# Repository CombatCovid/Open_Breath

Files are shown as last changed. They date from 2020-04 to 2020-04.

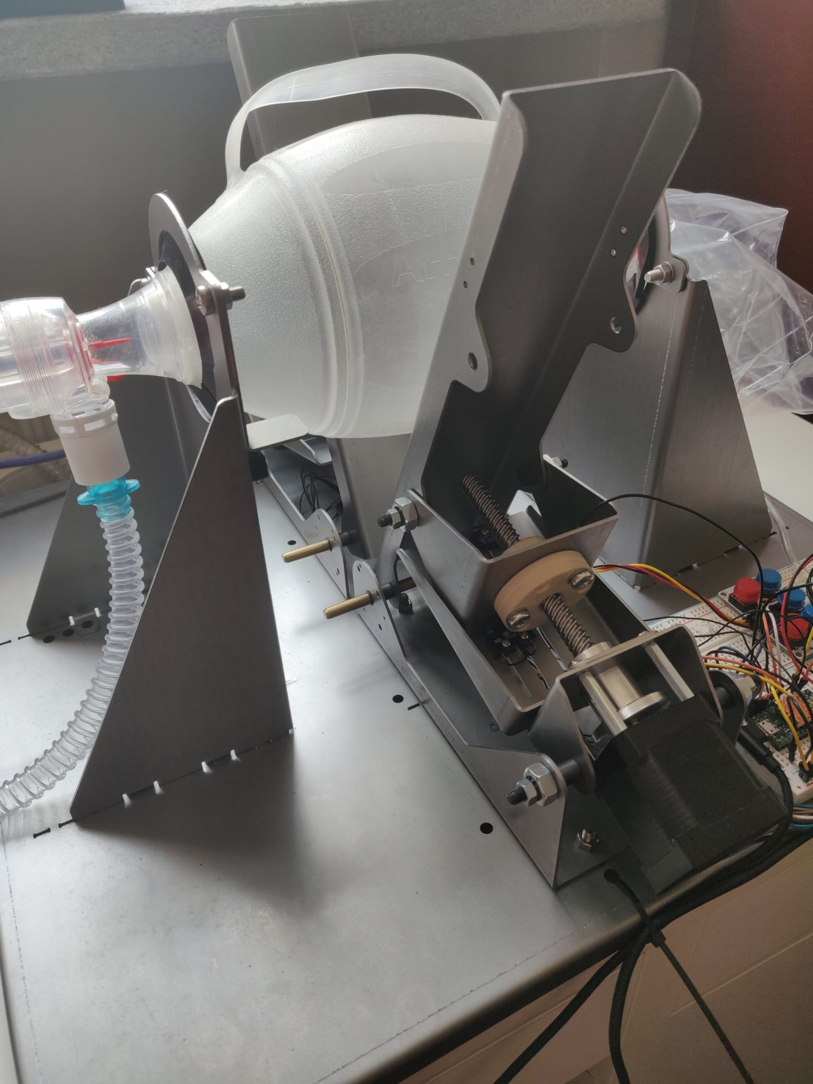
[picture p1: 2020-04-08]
docs/img/IMG-20200403-WA0022.jpg

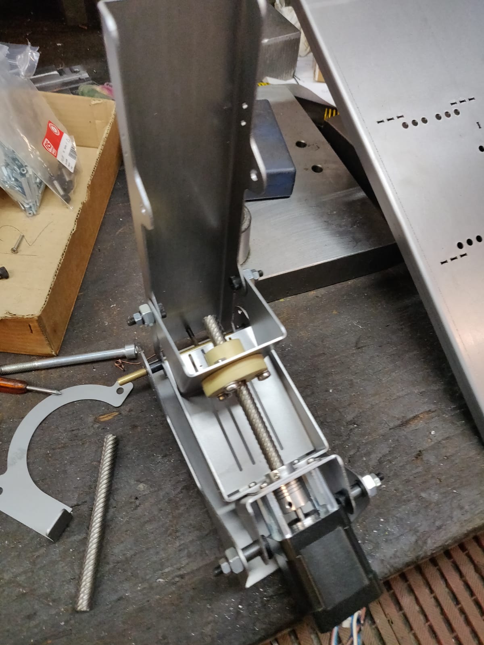
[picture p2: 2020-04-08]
docs/img/IMG-20200401-WA0078.jpg

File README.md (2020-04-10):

---
# n.b. metadata now goes in the metadata.yaml file, top level beside the repo README.md
---

# Title: OpenBreath Project



### References: 

All the information compiled here is from the [OpenBreath Project](https://www.openbreath.it/en/)

To download our repo: [**DOWNLOAD**](https://www.ohwr.org/project/openbreath/-/archive/master/openbreath-master.zip) <!-- Replace with github link -->

This is the url of our repo : [https://www.ohwr.org/project/openbreath/wikis/home/](https://www.ohwr.org/project/openbreath/wikis/home/) <!-- Replace with github link -->

### Background & Need

Open Breath project aims at the development and production of a scalable low-cost lung ventilator. Open Breath lung ventilator presents an innovative design, conceived to be quickly realized with off-the-shelflow-cost hardware components.

## Main Features
- Innovative design based on the automatization of a bag-valve-mask (BVM)
- Quickly producible with "off-the-shelf" parts
- Extremely low cost
- Both invasive and non-invasive assisted ventilation: PEEP, SIMV, CPAP modes
- Aims at compliance with the BS EN 80601-2-12:2020 standard
- Connected device and live interface:
- Sensors: pressure, flowrate
- Provides blood oxygenation rate and heart rate (nice to have)
- Will send alerts and updates in real-time directly to healthcare professionals
- We invite anyone who is interested to follow this work.

## Status of Development

The device is currently under development, a first metal prototype has been realized.



| Date   | Event |
| ----------- | ---------- |
| 01/03/2020  | Start of project in response to COVID-19 health emergency. Start on Openbreath.it  |
| 20/03/2020  | Need help from a Biomed apparatus certifier.  |
| 28/03/2020  | Need help from sheet metal workshop in and outside of Europe - first CAD Release Online  |
| 03/04/2020  | First Metal Prototype has been realized and the testing phase has started |

## How to replicate 

For assembeling the main body of the device sheet metal must be cut with a lasercutter and folded. 

DFX files for cutting can be downloaded [**HERE**](https://www.ohwr.org/project/openbreath/tree/master/CAD/DXF) <!-- Replace with github link -->

The hardware files for electronics can be downloaded [**HERE**](https://www.ohwr.org/project/openbreath/tree/master/Hardware) <!-- Replace with github link -->

The dashboard files can be download [**HERE**](https://www.ohwr.org/project/openbreath/tree/master/Dashboard) <!-- Replace with github link -->

<!-- # Steps to start documenting the equipment/design you found and chose 
[See this documentation example](https://github.com/CombatCovid/medical-shields-for-3d-printing). You can also download it to see the final result.
1. Download or clone this template to start documenting easily
2. Fill in the source files like STLS, CAD, etc inside

3. Use this one template to create new designs documentation
- Inside docs write down a simple README in language of choice.
- Put in the README.md the reference whre you got the source from to follow up.
- Write down steps to replicate if necessesary as well as guides in sequence.
If this part becomes difficult ask for help here in the [`#how-to-document-designs` channel ](https://discord.gg/QrAyWF)
 -->

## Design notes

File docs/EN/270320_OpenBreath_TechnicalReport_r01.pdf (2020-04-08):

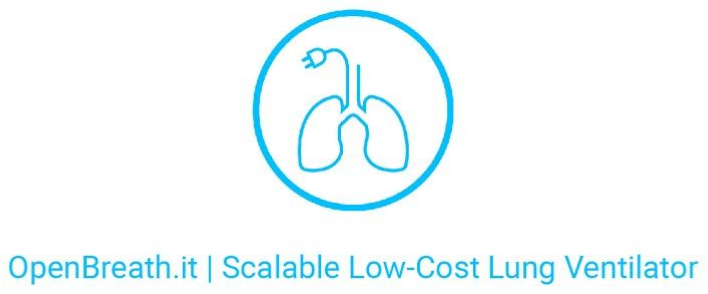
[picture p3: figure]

TOPIC: Technical Report_01 OpenBreath Device | 11:30 PM Friday, the 27th of March, 2020

This report aims to illustrate the features of the Open Breath lung ventilator, which is currently under

advanced development by our in-house team of designers and engineers. Being in the development

phase, the design may be subject to variations dictated by empirical requirements, which will be

established and proven as soon as possible by the in-depth testing phase of the device, and by the

public peer review phase.

The essential concept of the ventilator is the mechanical automation of a Bag Valve Mask (BVM), also

commonly known as Ambu® bag, a medical device used in manual resuscitation in hospitals all over

the world. We decided to use an Ambu bag as the pneumatic element of our ventilator for several

reasons. First of all, because of its proven operational effectiveness and its extensive availability as a

globally distributed, affordable component. It is also a certified medical device and can be easily

combined with all other medical devices needed to ensure proper patient ventilation.

The lung ventilator is composed of two identical and opposing four-link lever-screw mechanisms,

which synchronously compress an Ambu® self-expanding balloon (Fig. 1 label 6) equipped with a

PEEP valve. Each system consists of four laser-cut bent stainless steel plates (in fig. 1 labels 1, 2, 3,

4), a trapezoid screw (in fig. 1 label 2.c) and its lead nut (in fig. 1 label 3). a), a Nema 17 stepper

motor (in fig. 1 label 2.b) and two absolute or incremental rotary encoders, one axially positioned on

the motor shaft (in fig. 1 label 2.a) and the other one on the hinge of the presser (in fig. 1 label 5).

info@openbreath.it
www.openbreath.it

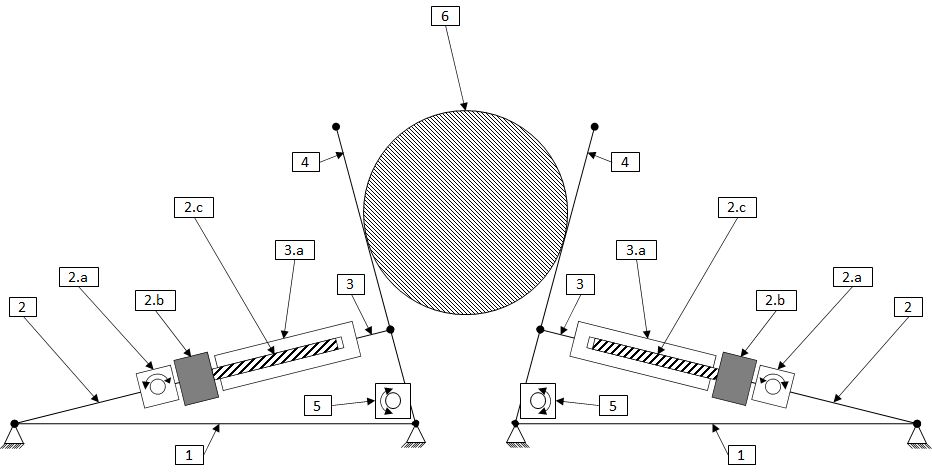
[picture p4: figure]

Figure 1.a - Scheme of the system in open position.

The encoders used can be both absolute and incremental according to the available supply. when incremental encoders are employed a homing operation will be carried out when the fan is switched on.

The stainless steel plates are hinged to each other by means of stainless steel pins and double flange IGUS technopolymer bushings, each axial sliding has a lifetime calculated by the manufacturer.

The trapezium screw and the lead nut are manufactured by IGUS, with calculated lifetime. The pressure application point of the lever-screw system is always tangent to the surface of the AMBU flask.

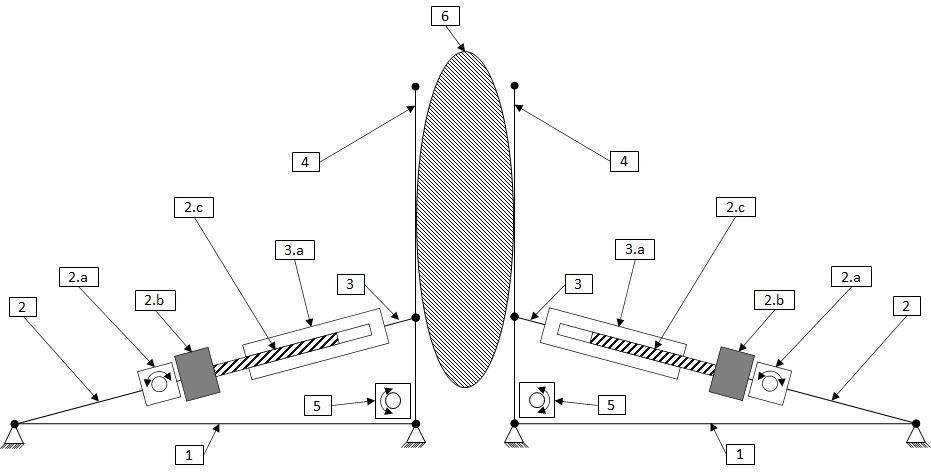
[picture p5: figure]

Figure 1.b -Scheme of the closed position systems.

The electronic system consists of a dual Motion Control (MC) system, a dual machine-operator interface system and a single embedded system used both for data display via web server and for alarm setting .

The single motion control system manages two stepper motors in open loop and supervises their movement by means of two absolute or incremental encoders, depending on the version in use. It also acquires pressure and air flow rate data via an I2C network.

The human-machine interface system takes care of acquiring the vital parameters from the operator and thereafter sends them to the motion control systems. Data is set by three incremental rotary encoders and a numeric keypad. The visualization is enabled by a LCD display, which includes an acoustic signal triggered by the set alarms.

The embedded system records all data, including the patient's vital parameters, and displays them on a web server application accessible from any device equipped with an internet browser (smartphones, tablets or PCs). In addition to this, it is possible to set alarms that will eventually be signalled both by the human-machine interface (HMI) and by the control panel hosted on the web server itself.

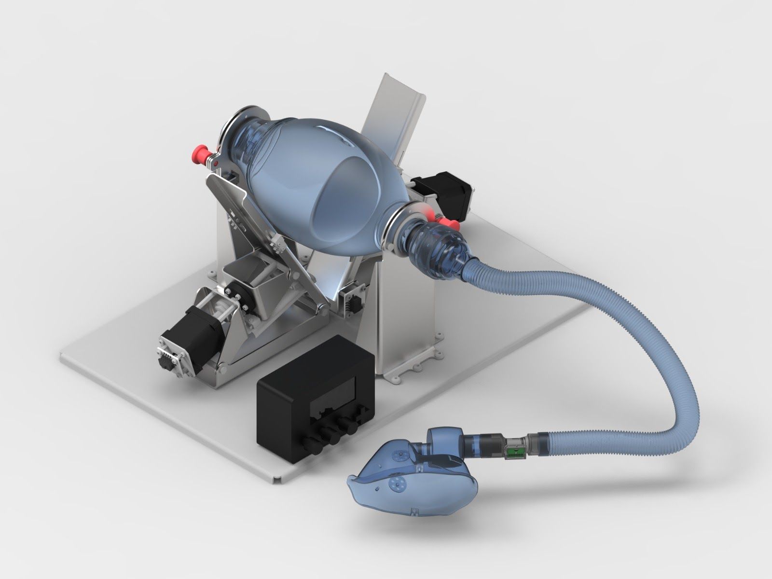
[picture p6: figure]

Fig. 2 - Overview, mechanics without external case.

M.C. systems, human-machine interface systems and sensors are completely redundant in all their components. This means that, in case of anomaly or failure of one of the boards, the remaining one takes absolute control over the system, guaranteeing its correct operation and immediately alerting the operator, who must promptly proceed to replace the ventilator.

In case one of the stepper motors fails, this will be deactivated, while the other one will increase the excursion and the speed of movement in order to keep the vital parameters output, set by the operator, unchanged. Contextually, the HMI system will warn the operator, who must replace the ventilator as soon as possible.

The motion control system acquires data from a pair of differential pressure sensors and a pair of flow meters, then compares the data of each pair and verifies that there are no discrepancies; otherwise, the HMI system will warn the operator.

The motion control system checks the effectiveness of the mechanical system by comparing the values of the encoder positioned on the motor shaft with those of the encoder positioned on the hinge shaft of the presser: if the deviations between the two values are too large, the HMI system warns the operator of a possible imminent mechanical fault.

The motion control system also regulates the air supplied to the patient according to two control modes:

1. CONSTANT PRESSURE:

The two pressors will compress the Ambu bag until the pressure threshold, set by the operator, is reached. A cut-off volume can also be selected at operator's discretion, when that level is reached, the ventilation cycle will be terminated.

2. CONSTANT VOLUME:

The two pressors will compress the Ambu until the volume threshold, set by the operator, is reached. A cut-off pressure can be selected at operator's discretion, when that level is reached, the ventilation cycle will be terminated.

These two control modes can be applied in two ventilation modes:

A. FULLY AUTOMATIC BREATHING:

In this mode, the frequency of ventilation is selected by the operator because the patient is unable to breathe independently.

B. ASSISTED RESPIRATION:

This mode of operation constantly monitors the flow of air-oxygen through flow meters. The patient's autonomic breathing is detected by increasing the monitored flow. When this occurs, the respirator pressors will compress the Ambu until the set pressure is reached and controlled by the pressure transducers.
When the motion control system detects a decrease in flow and a subsequent reversal of flow, the respirator goes into exhalation.

Positive end-expiratory pressure (PEEP) is regulated by a mechanical medical valve located near the Ambu outlet.

At this stage of development, the concentration of oxygen in the air supplied to the patient can be selected in three different sizes in this way:

- the concentration will be between 90% and 100% when using the Ambu with réservoir and oxygen tube connected to the oxygen distribution system of the hospital with flow between 12 and 15 lt/min;
- between 50% and 60% when using the Ambu connected to the oxygen tube without the réservoir;
- will be equal to the ambient concentration, or about 21% when used without réservoir or oxygen.

Note: The most accurate and efficient medical air-oxygen mixing system to be used with the Ambu system is still under study and will be subject to improvement before the final design is consolidated.

At present, the mechanical part is defined at 85%, so we expect to produce a prototype by March 29, 2020. After the latter we will start the development of the automatic controls and, if the system will meet the mechanical design requirements, we will freeze the mechanical design by starting the development of a plan for a production with medium runs. In parallel, we will accelerate software and electronic development.

Open Breath Team

Gabriel D’Anselmo

Simone Iannucci

Patrizio Cavarretta

Massimiliano D’Amario

Francesco Solinas

Vittoria Garosci

Francesco D’Anselmo

Roberto Caminati

Carlo Menegazzo

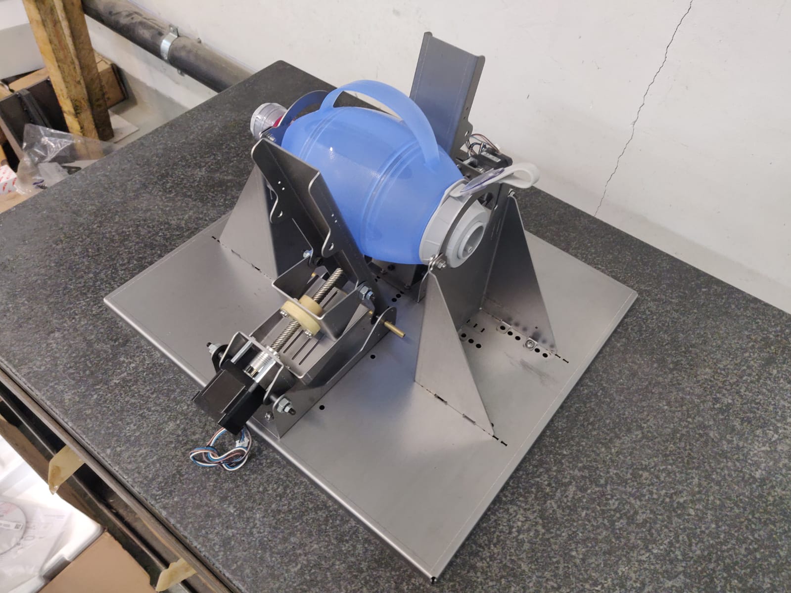
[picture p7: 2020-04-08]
docs/img/IMG-20200401-WA0064.jpg

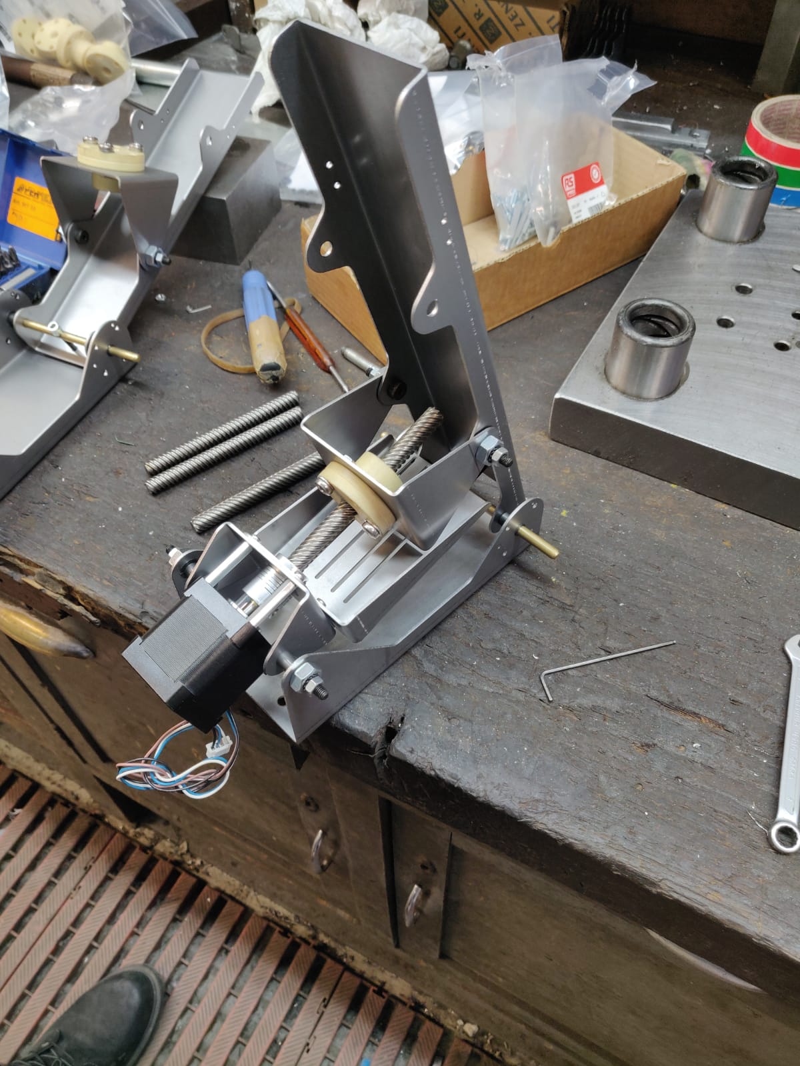
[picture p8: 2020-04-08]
docs/img/IMG-20200401-WA0073.jpg

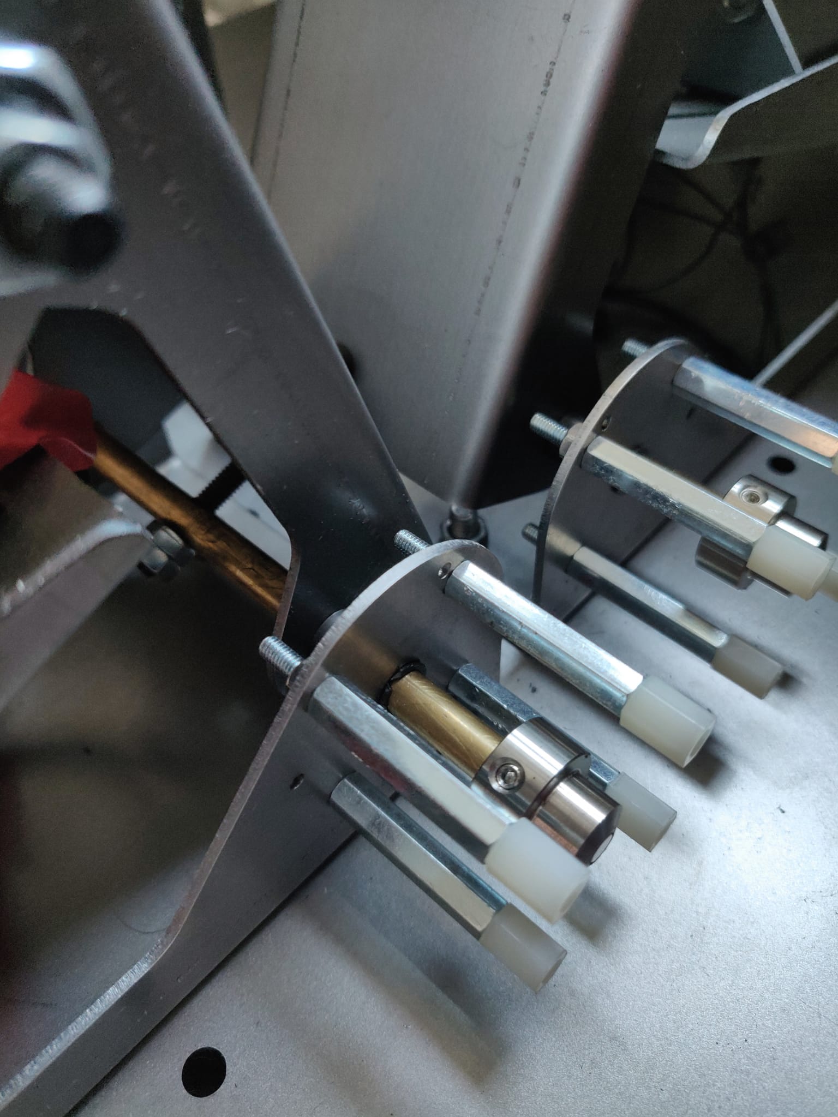
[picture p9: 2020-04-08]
docs/img/IMG-20200406-WA0024.jpg

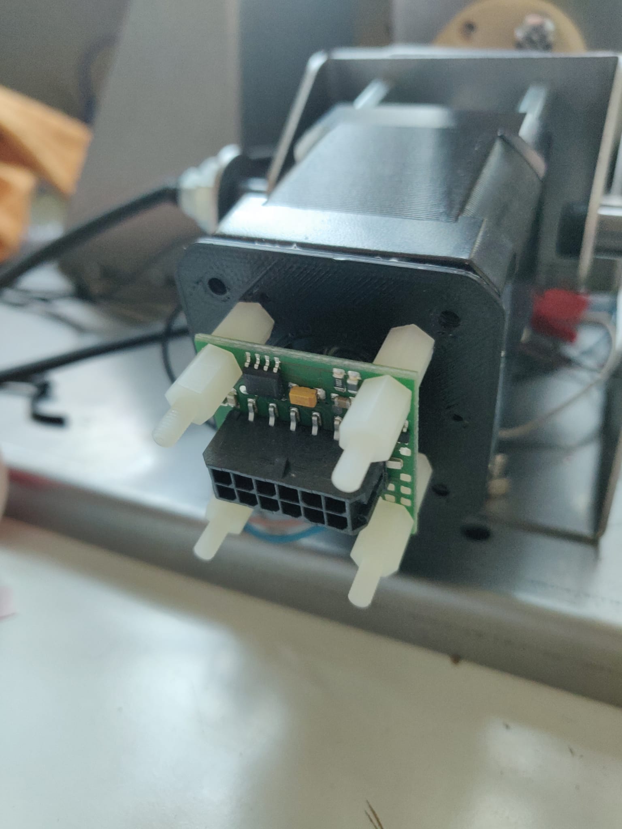
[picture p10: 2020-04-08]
docs/img/IMG-20200406-WA0020.jpg

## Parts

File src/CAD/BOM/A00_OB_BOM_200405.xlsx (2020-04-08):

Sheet: From Fusion 360
Part Name | Part Number | Make/Buy | Quantity | Assy
A00_OB_200404 | A00_OB_200404 |  | 1 | 3 | A00 | 3
P0008_OB_200401 | P0008_OB_200401 | Make | 1
A06_OB_200401 | A06_OB_200401 |  | 2
HELAVIA DG M75 | HELAVIA DG M75 | Buy | 2
P0009_OB_200401 | P0009_OB_200401 | Make | 2
P0010_OB_200401 | P0010_OB_200401 | Make | 2
Washer_M6 | Washer_M6 | Buy | 8
Screw_M6_14 | Screw_M6_14 | Buy | 4
Nut_M6 | Nut_M6 | Buy | 4
Omron_LimitSwitch_20834 | LimitSwitch | Buy | 16
Washer_M3 | Washer_M3 | Buy | 8
Screw_M3_20 | Screw_M3_20 | Buy | 4
Nut_M3 | Nut_M3 | Buy | 4
A01_OB_200401 | A01_OB_200401 |  | 2
A03_OB_200401 | A03_OB_200401 |  | 2
Igus_MCM_06_015_1 | Igus_MCM_06_015_1 | Buy | 12
P0001_OB_200401 | P0001_OB_200401 | Make | 2
WE_M3_20_971200354 | Standoffs_M3_20 | Buy | 8
Washer_M3 | Washer_M3 | Buy | 8
Nut_M3 | Nut_M3 | Buy | 8
WE_Standoffs_M2_15_971150244 | Standoffs_M2_15 | Buy | 6
Washer_M2 | Washer_M2 | Buy | 6
Nut_M2 | Nut_M2 | Buy | 6
P0007_OB_200401 | P0007_OB_200401 | Make | 2
RLS - BA060AB01AA00 | RLS - BA060AB01AA00 | Buy | 2
RLS - BR10xxx14xxxxD00 | RLS - BR10xxx14xxxxD00 | Buy | 2
Screw_M2_5_Phillips | Screw_M2_5_Phillips | Buy | 6
RLS - RMA06A3A00 | RLS - RMA06A3A00 | Buy | 2
RLS - RMB29AC01SS | RLS - RMB29AC01SS | Buy | 4
Screw_M3_Phillips/Countersunk | Screw_M3_5_Phillips/Countersunk | Buy | 8
A05_OB_200402 | A05_OB_200402 |  | 2
P0003_OB_200401 | P0003_OB_200401 | Make | 2
A07_LimitSwitch | A07_LimitSwitch |  | 12
Washer_M2 | Washer_M2 | Buy | 48
Nut_M2 | Nut_M2 | Buy | 24
Screw_M2_12 | Screw_M2_12 | Buy | 24
Screw_M3_25 | Screw_M3_25 | Buy | 2
A02_OB_200404 | A02_OB_200404 |  | 2
P0002_OB_200404 | P0002_OB_200404 | Make | 2
P0005_OB_200403 | P0005_OB_200403 | Make | 2
Igus_NEMA_23_MOT-AN-S-060-020-056-L-A-AAAA | Igus_NEMA_23_MOT-AN-S-060-020-056-L-A-AAAA | Buy | 2
ShaftCoupler_6.35_6.00 | ShaftCoupler_6.35_6.00 | Buy | 2
Set_Screw_M4 | Set_Screw_M4 | Buy | 8
Igus_DST-LS-10x12-R-200-ES_Parametric | Igus_DST-LS-10x12-R-200-ES_Parametric | Buy | 2
AutomotionComponents - L1390.FK06 | AutomotionComponents - L1390.FK06 | Buy | 2
P0006_OB_200403 | P0006_OB_200403 | Make | 2
Washer_M3 | Washer_M3 | Buy | 24
Screw_M3_14 | Screw_M3_14 | Buy | 8
Nut_M3 | Nut_M3 | Buy | 16
Washer_M4 | Washer_M4 | Buy | 16
Nut_M4 | Nut_M4 | Buy | 8
Screw_M4_60 | Screw_M4_60 | Buy | 8
Spacer_M4_45 | Spacer_M4_45 | Buy | 8
RLS - RMH06A3A02 | RLS - RMH06A3A02 | Buy | 2
Standoffs_M3_8 | Standoffs_M3_8 | Buy | 8
WE_Spacer_2.5_3.3_6_9774025960_rev1 | Spacer_2.5_3.3_6 | Buy | 8
Washer_M3_Plastic | Washer_M3_Plastic | Buy | 8
Screw_M3_5_Phillips | Screw_M3_5_Phillips | Buy | 8
Screw_M3_10 | Screw_M3_10 | Buy | 8
A04_OB_200401 | A04_OB_200401 |  | 2
P0004_OB_200401 | P0004_OB_200401 | Make | 2
Igus_DST-JFRM-2525DS10x12 | Igus_DST-JFRM-2525DS10x12 | Buy | 2
Washer_M5 | Washer_M5 | Buy | 12
Screw_M5_20 | Screw_M5_20 | Buy | 12
Nut_M5 | Nut_M5 | Buy | 12
Seeger_6 | Seeger_6 | Buy | 8
Igus_MSM-0608-10 | Igus_MSM-0608-10 | Buy | 4
Washer_M6 | Washer_M6 | Buy | 16
Nut_M5 | Nut_M5 | Buy | 8
Screw_M5_Shoulder_6_6 | Screw_M5_Shoulder_6_6 | Buy | 8
Ambu_Spur_II_200313 | Ambu_Spur_II_200313 | Buy | 1
Washer_M6 | Washer_M6 | Buy | 36
Nut_M6 | Nut_M6 | Buy | 18
Screw_M6_14 | Screw_M6_14 | Buy | 18

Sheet: BOM_A00_200405
Make/Buy | Make
Row Labels | Sum of Quantity
P0001_OB_200401 | 2
P0002_OB_200404 | 2
P0003_OB_200401 | 2
P0004_OB_200401 | 2
P0005_OB_200403 | 2
P0006_OB_200403 | 2
P0007_OB_200401 | 2
P0008_OB_200401 | 1
P0009_OB_200401 | 2
P0010_OB_200401 | 2
Grand Total | 19

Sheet: Buy
Make/Buy | Buy
Row Labels | Sum of Quantity
Ambu_Spur_II_200313 | 1
AutomotionComponents - L1390.FK06 | 2
HELAVIA DG M75 | 2
Igus_DST-JFRM-2525DS10x12 | 2
Igus_DST-LS-10x12-R-200-ES_Parametric | 2
Igus_MCM_06_015_1 | 12
Igus_MSM-0608-10 | 4
Igus_NEMA_23_MOT-AN-S-060-020-056-L-A-AAAA | 2
LimitSwitch (Omron_LimitSwitch_20834) | 16
Nut_M2 | 30
Nut_M3 | 28
Nut_M4 | 8
Nut_M5 | 20
Nut_M6 | 22
RLS - BA060AB01AA00 | 2
RLS - BR10xxx14xxxxD00 | 2
RLS - RMA06A3A00 | 2
RLS - RMB29AC01SS | 4
RLS - RMH06A3A02 | 2
Screw_M2_12 | 24
Screw_M2_5_Phillips | 6
Screw_M3_10 | 8
Screw_M3_14 | 8
Screw_M3_20 | 4
Screw_M3_25 | 2
Screw_M3_5_Phillips | 8
Screw_M3_5_Phillips/Countersunk (Screw_M3_Phillips/Countersunk) | 8
Screw_M4_60 | 8
Screw_M5_20 | 12
Screw_M5_Shoulder_6_6 | 8
Screw_M6_14 | 22
Seeger_6 | 8
Set_Screw_M4 | 8
ShaftCoupler_6.35_6.00 | 2
Spacer_2.5_3.3_6 (WE_Spacer_2.5_3.3_6_9774025960_rev1) | 8
Spacer_M4_45 | 8
Standoffs_M2_15 (WE_Standoffs_M2_15_971150244) | 6
Standoffs_M3_20 (WE_M3_20_971200354) | 8
Standoffs_M3_8 | 8
Washer_M2 | 54
Washer_M3 | 40
Washer_M3_Plastic | 8
Washer_M4 | 16
Washer_M5 | 12
Washer_M6 | 60
Grand Total | 527

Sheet: Make
Make/Buy | Make
Row Labels | Sum of Quantity
P0001_OB_200401 | 2
P0002_OB_200404 | 2
P0003_OB_200401 | 2
P0004_OB_200401 | 2
P0005_OB_200403 | 2
P0006_OB_200403 | 2
P0007_OB_200401 | 2
P0008_OB_200401 | 1
P0009_OB_200401 | 2
P0010_OB_200401 | 2
Grand Total | 19

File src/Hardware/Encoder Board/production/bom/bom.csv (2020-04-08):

Item | Quantity | Reference | Part | PCB Footprint | Device
______________________________________________
1 | 3 | BR1 | CIRCUIT BREAKER | cap0402
 |  | BR2 | CIRCUIT BREAKER | cap0402
 |  | BR3 | CIRCUIT BREAKER | cap0402
2 | 2 | C1 | 100n | smc0603 | 06035C104K4T2A
 |  | C2 | 100n | smc0603 | 06035C104K4T2A
3 | 1 | C3 | 10u | cap0805 | GRM188R6YA106MA73D
4 | 1 | J1 | S20B-PADSS-1(LF)(SN) | JST_PADSS_90deg_10x2 | S20B-PADSS-1(LF)(SN)
5 | 1 | L1 | BLM18PG300SN1D | res0603 | BLM18PG300SN1D
6 | 3 | R1 | 51k | res0603 | CRCW060351K0FKEA
 |  | R2 | 51k | res0603 | CRCW060351K0FKEA
 |  | R3 | 51k | res0603 | CRCW060351K0FKEA
7 | 1 | U1 | AM4096 | SSOP28-LD | AM4096
8 | 1 | J1-housing | PADP-20V-1-S | JST_ | PADP-20V-1-S
9 | 20 | J1pin | SPH-001T-P0.5L | contacts | SPH-001T-P0.5L

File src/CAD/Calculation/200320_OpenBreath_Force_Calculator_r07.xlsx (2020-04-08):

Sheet: ALL (Table) (NEMA 17)
Durata d'esercizio min. Doppie corse | Durata d'esercizio min. Giorni | Requ. Coppia | Filettatura D1 x P | Filettatura | D1 | Principi | Passo | Madrevite Materiale | d2 | b1 | Prezzo/pz. | Vite Materiale | Prezzo/m | Forza assiale dinamica (continua) | Corsa | Velocità di avanzamento | RPM | Tempo di funzionamento | Madrevite Codice art. | Vite Codice art.
#N/A | #N/A | 0.9 N/m | Ds16x35 | Ds | 16 mm | #N/A | 35 mm | J200 | 28 mm | 35 mm | €37.11 | Acciaio inox | €120.54 | 80 N | 33 mm | 2.3 m/min | 66 | 100%
#N/A | #N/A | 3.0 N/m | Ds18x100 | Ds | 18 mm | #N/A | 100 mm | J200 | 28 mm | 35 mm | €38.22 | Acciaio inox | €146.70 | 80 N | 33 mm | 2.3 m/min | 23.1 | 100%
#N/A | #N/A | 0.7 N/m | Ds18x24 | Ds | 18 mm | #N/A | 24 mm | J200 | 28 mm | 35 mm | €37.48 | Acciaio inox | €146.37 | 80 N | 33 mm | 2.3 m/min | 96.25 | 100%
#N/A | #N/A | 1.1 N/m | Ds18x40 | Ds | 18 mm | #N/A | 40 mm | J200 | 28 mm | 35 mm | €37.86 | Acciaio inox | €134.07 | 80 N | 33 mm | 2.3 m/min | 57.75 | 100%
#N/A | #N/A | 2.4 N/m | Ds18x80 | Ds | 18 mm | #N/A | 80 mm | J200 | 28 mm | 35 mm | €38.04 | Acciaio inox | €139.40 | 80 N | 33 mm | 2.3 m/min | 28.875 | 100%
#N/A | #N/A | 0.6 N/m | Ds20x20 | Ds | 20 mm | #N/A | 20 mm | J200 | 32 mm | 44 mm | €43.75 | Acciaio inox | €154.98 | 80 N | 33 mm | 2.3 m/min | 115.5 | 100%
#N/A | #N/A | 1.3 N/m | Ds20x50 | Ds | 20 mm | #N/A | 50 mm | J200 | 32 mm | 44 mm | €44.19 | Alluminio | Su richiesta | 80 N | 33 mm | 2.3 m/min | 46.2 | 100%
#N/A | #N/A | 1.3 N/m | Ds20x50 | Ds | 20 mm | #N/A | 50 mm | J200 | 32 mm | 44 mm | €44.19 | Acciaio inox | €156.78 | 80 N | 33 mm | 2.3 m/min | 46.2 | 100%
#N/A | #N/A | 1.7 N/m | Ds20x60 | Ds | 20 mm | #N/A | 60 mm | J200 | 32 mm | 44 mm | €44.63 | Acciaio inox | €158.26 | 80 N | 33 mm | 2.3 m/min | 38.5 | 100%
#N/A | #N/A | 2.2 N/m | Ds20x80 | Ds | 20 mm | #N/A | 80 mm | J200 | 32 mm | 44 mm | €45.08 | Acciaio inox | €164.82 | 80 N | 33 mm | 2.3 m/min | 28.875 | 100%
#N/A | #N/A | 2.7 N/m | Ds20x90 | Ds | 20 mm | #N/A | 90 mm | J200 | 32 mm | 44 mm | €45.53 | Acciaio inox | €167.28 | 80 N | 33 mm | 2.3 m/min | 25.66666667 | 100%
#N/A | #N/A | 1.4 N/m | Ds16x35 | Ds | 16 mm | #N/A | 35 mm | J200 | 28 mm | 35 mm | €37.11 | Acciaio inox | €120.54 | 120 N | 22 mm | 1.5 m/min | 44 | 100%
#N/A | #N/A | 4.5 N/m | Ds18x100 | Ds | 18 mm | #N/A | 100 mm | J200 | 28 mm | 35 mm | €38.22 | Acciaio inox | €146.70 | 120 N | 22 mm | 1.5 m/min | 15.4 | 100%
#N/A | #N/A | 1.0 N/m | Ds18x24 | Ds | 18 mm | #N/A | 24 mm | J200 | 28 mm | 35 mm | €37.48 | Acciaio inox | €146.37 | 120 N | 22 mm | 1.5 m/min | 64.16666667 | 100%
#N/A | #N/A | 1.6 N/m | Ds18x40 | Ds | 18 mm | #N/A | 40 mm | J200 | 28 mm | 35 mm | €37.86 | Acciaio inox | €134.07 | 120 N | 22 mm | 1.5 m/min | 38.5 | 100%
#N/A | #N/A | 3.5 N/m | Ds18x80 | Ds | 18 mm | #N/A | 80 mm | J200 | 28 mm | 35 mm | €38.04 | Acciaio inox | €139.40 | 120 N | 22 mm | 1.5 m/min | 19.25 | 100%
#N/A | #N/A | 0.9 N/m | Ds20x20 | Ds | 20 mm | #N/A | 20 mm | J200 | 32 mm | 44 mm | €43.75 | Acciaio inox | €154.98 | 120 N | 22 mm | 1.5 m/min | 77 | 100%
#N/A | #N/A | 2.0 N/m | Ds20x50 | Ds | 20 mm | #N/A | 50 mm | J200 | 32 mm | 44 mm | €44.19 | Alluminio | Su richiesta | 120 N | 22 mm | 1.5 m/min | 30.8 | 100%
#N/A | #N/A | 2.0 N/m | Ds20x50 | Ds | 20 mm | #N/A | 50 mm | J200 | 32 mm | 44 mm | €44.19 | Acciaio inox | €156.78 | 120 N | 22 mm | 1.5 m/min | 30.8 | 100%
#N/A | #N/A | 2.4 N/m | Ds20x60 | Ds | 20 mm | #N/A | 60 mm | J200 | 32 mm | 44 mm | €44.63 | Acciaio inox | €158.26 | 120 N | 22 mm | 1.5 m/min | 25.66666667 | 100%
#N/A | #N/A | 3.2 N/m | Ds20x80 | Ds | 20 mm | #N/A | 80 mm | J200 | 32 mm | 44 mm | €45.08 | Acciaio inox | €164.82 | 120 N | 22 mm | 1.5 m/min | 19.25 | 100%
#N/A | #N/A | 4.0 N/m | Ds20x90 | Ds | 20 mm | #N/A | 90 mm | J200 | 32 mm | 44 mm | €45.53 | Acciaio inox | €167.28 | 120 N | 22 mm | 1.5 m/min | 17.11111111 | 100%
#N/A | #N/A | 0.5 N/m | Tr16x4 | Tr | 16 mm | #N/A | 4 mm | J200 | 28 mm | 35 mm | €32.40 | Acciaio C15 | €19.09 | 120 N | 22 mm | 1.5 m/min | 385 | 100%
#N/A | #N/A | 0.5 N/m | Tr16x4 | Tr | 16 mm | #N/A | 4 mm | J200 | 28 mm | 35 mm | €32.40 | Acciaio inox | €74.98 | 120 N | 22 mm | 1.5 m/min | 385 | 100%
#N/A | #N/A | 0.6 N/m | Tr16x8P4 | Tr | 16 mm | 8 | 4 mm | J200 | 28 mm | 35 mm | €33.04 | Acciaio C15 | €19.09 | 120 N | 22 mm | 1.5 m/min | 385 | 100%
#N/A | #N/A | 0.6 N/m | Tr16x8P4 | Tr | 16 mm | 8 | 4 mm | J200 | 28 mm | 35 mm | €33.04 | Acciaio inox | €99.59 | 120 N | 22 mm | 1.5 m/min | 385 | 100%
#N/A | #N/A | 0.5 N/m | Tr18x4 | Tr | 18 mm | #N/A | 4 mm | J200 | 28 mm | 35 mm | €36.35 | Acciaio C15 | €25.99 | 120 N | 22 mm | 1.5 m/min | 385 | 100%
#N/A | #N/A | 0.5 N/m | Tr18x4 | Tr | 18 mm | #N/A | 4 mm | J200 | 28 mm | 35 mm | €36.35 | Acciaio inox | €92.69 | 120 N | 22 mm | 1.5 m/min | 385 | 100%
#N/A | #N/A | 0.6 N/m | Tr18x8P4 | Tr | 18 mm | 8 | 4 mm | J200 | 28 mm | 35 mm | €37.07 | Acciaio C15 | €27.37 | 120 N | 22 mm | 1.5 m/min | 385 | 100%
#N/A | #N/A | 0.6 N/m | Tr18x8P4 | Tr | 18 mm | 8 | 4 mm | J200 | 28 mm | 35 mm | €37.07 | Acciaio inox | €143.29 | 120 N | 22 mm | 1.5 m/min | 385 | 100%
#N/A | #N/A | 0.5 N/m | Tr20x4 | Tr | 20 mm | #N/A | 4 mm | J200 | 32 mm | 44 mm | €37.82 | Acciaio C15 | €28.29 | 120 N | 22 mm | 1.5 m/min | 385 | 100%
#N/A | #N/A | 0.5 N/m | Tr20x4 | Tr | 20 mm | #N/A | 4 mm | J200 | 32 mm | 44 mm | €37.82 | Acciaio inox | €124.89 | 120 N | 22 mm | 1.5 m/min | 385 | 100%
#N/A | #N/A | 0.6 N/m | Tr20x8P4 | Tr | 20 mm | 8 | 4 mm | J200 | 32 mm | 44 mm | €38.57 | Acciaio C15 | €28.29 | 120 N | 22 mm | 1.5 m/min | 385 | 100%
#N/A | #N/A | 0.6 N/m | Tr20x8P4 | Tr | 20 mm | 8 | 4 mm | J200 | 32 mm | 44 mm | €38.57 | Acciaio inox | €147.89 | 120 N | 22 mm | 1.5 m/min | 385 | 100%
#N/A | #N/A | 0.6 N/m | Tr24x5 | Tr | 24 mm | #N/A | 5 mm | J200 | 32 mm | 44 mm | €40.50 | Acciaio C15 | €34.82 | 120 N | 22 mm | 1.5 m/min | 308 | 100%
#N/A | #N/A | 0.6 N/m | Tr24x5 | Tr | 24 mm | #N/A | 5 mm | J200 | 32 mm | 44 mm | €40.50 | Acciaio inox | €147.52 | 120 N | 22 mm | 1.5 m/min | 308 | 100%
#N/A | #N/A | 2.7 N/m | Ds16x35 | Ds | 16 mm | #N/A | 35 mm | J200 | 28 mm | 35 mm | €37.11 | Acciaio inox | €120.54 | 240 N | 11 mm | 0.8 m/min | 22 | 100%
#N/A | #N/A | 8.9 N/m | Ds18x100 | Ds | 18 mm | #N/A | 100 mm | J200 | 28 mm | 35 mm | €38.22 | Acciaio inox | €146.70 | 240 N | 11 mm | 0.8 m/min | 7.7 | 100%
#N/A | #N/A | 2.0 N/m | Ds18x24 | Ds | 18 mm | #N/A | 24 mm | J200 | 28 mm | 35 mm | €37.48 | Acciaio inox | €146.37 | 240 N | 11 mm | 0.8 m/min | 32.08333333 | 100%
#N/A | #N/A | 3.1 N/m | Ds18x40 | Ds | 18 mm | #N/A | 40 mm | J200 | 28 mm | 35 mm | €37.86 | Acciaio inox | €134.07 | 240 N | 11 mm | 0.8 m/min | 19.25 | 100%
#N/A | #N/A | 7.0 N/m | Ds18x80 | Ds | 18 mm | #N/A | 80 mm | J200 | 28 mm | 35 mm | €38.04 | Acciaio inox | €139.40 | 240 N | 11 mm | 0.8 m/min | 9.625 | 100%
#N/A | #N/A | 1.8 N/m | Ds20x20 | Ds | 20 mm | #N/A | 20 mm | J200 | 32 mm | 44 mm | €43.75 | Acciaio inox | €154.98 | 240 N | 11 mm | 0.8 m/min | 38.5 | 100%
#N/A | #N/A | 3.8 N/m | Ds20x50 | Ds | 20 mm | #N/A | 50 mm | J200 | 32 mm | 44 mm | €44.19 | Alluminio | Su richiesta | 240 N | 11 mm | 0.8 m/min | 15.4 | 100%
#N/A | #N/A | 3.8 N/m | Ds20x50 | Ds | 20 mm | #N/A | 50 mm | J200 | 32 mm | 44 mm | €44.19 | Acciaio inox | €156.78 | 240 N | 11 mm | 0.8 m/min | 15.4 | 100%
#N/A | #N/A | 4.8 N/m | Ds20x60 | Ds | 20 mm | #N/A | 60 mm | J200 | 32 mm | 44 mm | €44.63 | Acciaio inox | €158.26 | 240 N | 11 mm | 0.8 m/min | 12.83333333 | 100%
#N/A | #N/A | 6.4 N/m | Ds20x80 | Ds | 20 mm | #N/A | 80 mm | J200 | 32 mm | 44 mm | €45.08 | Acciaio inox | €164.82 | 240 N | 11 mm | 0.8 m/min | 9.625 | 100%
#N/A | #N/A | 7.9 N/m | Ds20x90 | Ds | 20 mm | #N/A | 90 mm | J200 | 32 mm | 44 mm | €45.53 | Acciaio inox | €167.28 | 240 N | 11 mm | 0.8 m/min | 8.555555556 | 100%
#N/A | #N/A | 0.9 N/m | Tr16x4 | Tr | 16 mm | #N/A | 4 mm | J200 | 28 mm | 35 mm | €32.40 | Acciaio C15 | €19.09 | 240 N | 11 mm | 0.8 m/min | 192.5 | 100%
#N/A | #N/A | 0.9 N/m | Tr16x4 | Tr | 16 mm | #N/A | 4 mm | J200 | 28 mm | 35 mm | €32.40 | Acciaio inox | €74.98 | 240 N | 11 mm | 0.8 m/min | 192.5 | 100%
#N/A | #N/A | 1.1 N/m | Tr16x8P4 | Tr | 16 mm | 8 | 4 mm | J200 | 28 mm | 35 mm | €33.04 | Acciaio C15 | €19.09 | 240 N | 11 mm | 0.8 m/min | 192.5 | 100%
#N/A | #N/A | 1.1 N/m | Tr16x8P4 | Tr | 16 mm | 8 | 4 mm | J200 | 28 mm | 35 mm | €33.04 | Acciaio inox | €99.59 | 240 N | 11 mm | 0.8 m/min | 192.5 | 100%
#N/A | #N/A | 1.0 N/m | Tr18x4 | Tr | 18 mm | #N/A | 4 mm | J200 | 28 mm | 35 mm | €36.35 | Acciaio C15 | €25.99 | 240 N | 11 mm | 0.8 m/min | 192.5 | 100%
#N/A | #N/A | 1.0 N/m | Tr18x4 | Tr | 18 mm | #N/A | 4 mm | J200 | 28 mm | 35 mm | €36.35 | Acciaio inox | €92.69 | 240 N | 11 mm | 0.8 m/min | 192.5 | 100%
#N/A | #N/A | 1.2 N/m | Tr18x8P4 | Tr | 18 mm | 8 | 4 mm | J200 | 28 mm | 35 mm | €37.07 | Acciaio C15 | €27.37 | 240 N | 11 mm | 0.8 m/min | 192.5 | 100%
#N/A | #N/A | 1.2 N/m | Tr18x8P4 | Tr | 18 mm | 8 | 4 mm | J200 | 28 mm | 35 mm | €37.07 | Acciaio inox | €143.29 | 240 N | 11 mm | 0.8 m/min | 192.5 | 100%
#N/A | #N/A | 1.0 N/m | Tr20x4 | Tr | 20 mm | #N/A | 4 mm | J200 | 32 mm | 44 mm | €37.82 | Acciaio C15 | €28.29 | 240 N | 11 mm | 0.8 m/min | 192.5 | 100%
#N/A | #N/A | 1.0 N/m | Tr20x4 | Tr | 20 mm | #N/A | 4 mm | J200 | 32 mm | 44 mm | €37.82 | Acciaio inox | €124.89 | 240 N | 11 mm | 0.8 m/min | 192.5 | 100%
#N/A | #N/A | 1.2 N/m | Tr20x8P4 | Tr | 20 mm | 8 | 4 mm | J200 | 32 mm | 44 mm | €38.57 | Acciaio C15 | €28.29 | 240 N | 11 mm | 0.8 m/min | 192.5 | 100%
#N/A | #N/A | 1.2 N/m | Tr20x8P4 | Tr | 20 mm | 8 | 4 mm | J200 | 32 mm | 44 mm | €38.57 | Acciaio inox | €147.89 | 240 N | 11 mm | 0.8 m/min | 192.5 | 100%
#N/A | #N/A | 1.2 N/m | Tr24x5 | Tr | 24 mm | #N/A | 5 mm | J200 | 32 mm | 44 mm | €40.50 | Acciaio C15 | €34.82 | 240 N | 11 mm | 0.8 m/min | 154 | 100%
#N/A | #N/A | 1.2 N/m | Tr24x5 | Tr | 24 mm | #N/A | 5 mm | J200 | 32 mm | 44 mm | €40.50 | Acciaio inox | €147.52 | 240 N | 11 mm | 0.8 m/min | 154 | 100%
#N/A | #N/A | 0.3 N/m | Tr16x4 | Tr | 16 mm | #N/A | 4 mm | J200 | 28 mm | 35 mm | €32.40 | Acciaio C15 | €19.09 | 80 N | 33 mm | 2.3 m/min | 577.5 | 100%
#N/A | #N/A | 0.3 N/m | Tr16x4 | Tr | 16 mm | #N/A | 4 mm | J200 | 28 mm | 35 mm | €32.40 | Acciaio inox | €74.98 | 80 N | 33 mm | 2.3 m/min | 577.5 | 100%
#N/A | #N/A | 0.4 N/m | Tr16x8P4 | Tr | 16 mm | 8 | 4 mm | J200 | 28 mm | 35 mm | €33.04 | Acciaio C15 | €19.09 | 80 N | 33 mm | 2.3 m/min | 577.5 | 100%
#N/A | #N/A | 0.4 N/m | Tr16x8P4 | Tr | 16 mm | 8 | 4 mm | J200 | 28 mm | 35 mm | €33.04 | Acciaio inox | €99.59 | 80 N | 33 mm | 2.3 m/min | 577.5 | 100%
#N/A | #N/A | 0.4 N/m | Tr18x4 | Tr | 18 mm | #N/A | 4 mm | J200 | 28 mm | 35 mm | €36.35 | Acciaio C15 | €25.99 | 80 N | 33 mm | 2.3 m/min | 577.5 | 100%
#N/A | #N/A | 0.4 N/m | Tr18x4 | Tr | 18 mm | #N/A | 4 mm | J200 | 28 mm | 35 mm | €36.35 | Acciaio inox | €92.69 | 80 N | 33 mm | 2.3 m/min | 577.5 | 100%
#N/A | #N/A | 0.4 N/m | Tr18x8P4 | Tr | 18 mm | 8 | 4 mm | J200 | 28 mm | 35 mm | €37.07 | Acciaio C15 | €27.37 | 80 N | 33 mm | 2.3 m/min | 577.5 | 100%
#N/A | #N/A | 0.4 N/m | Tr18x8P4 | Tr | 18 mm | 8 | 4 mm | J200 | 28 mm | 35 mm | €37.07 | Acciaio inox | €143.29 | 80 N | 33 mm | 2.3 m/min | 577.5 | 100%
#N/A | #N/A | 0.4 N/m | Tr20x4 | Tr | 20 mm | #N/A | 4 mm | J200 | 32 mm | 44 mm | €37.82 | Acciaio C15 | €28.29 | 80 N | 33 mm | 2.3 m/min | 577.5 | 100%
#N/A | #N/A | 0.4 N/m | Tr20x4 | Tr | 20 mm | #N/A | 4 mm | J200 | 32 mm | 44 mm | €37.82 | Acciaio inox | €124.89 | 80 N | 33 mm | 2.3 m/min | 577.5 | 100%
#N/A | #N/A | 0.4 N/m | Tr20x8P4 | Tr | 20 mm | 8 | 4 mm | J200 | 32 mm | 44 mm | €38.57 | Acciaio C15 | €28.29 | 80 N | 33 mm | 2.3 m/min | 577.5 | 100%
#N/A | #N/A | 0.4 N/m | Tr20x8P4 | Tr | 20 mm | 8 | 4 mm | J200 | 32 mm | 44 mm | €38.57 | Acciaio inox | €147.89 | 80 N | 33 mm | 2.3 m/min | 577.5 | 100%
#N/A | #N/A | 0.4 N/m | Tr24x5 | Tr | 24 mm | #N/A | 5 mm | J200 | 32 mm | 44 mm | €40.50 | Acciaio C15 | €34.82 | 80 N | 33 mm | 2.3 m/min | 462 | 100%
#N/A | #N/A | 0.4 N/m | Tr24x5 | Tr | 24 mm | #N/A | 5 mm | J200 | 32 mm | 44 mm | €40.50 | Acciaio inox | €147.52 | 80 N | 33 mm | 2.3 m/min | 462 | 100%
41031294 | 814.1129762 Day | 0.6 N/m | Ds20x20 | Ds | 20 mm | #N/A | 20 mm | J200 | 32 mm | 44 mm | €43.75 | Alluminio | €270.00 | 80 N | 33 mm | 2.3 m/min | 115.5 | 100%
41031294 | 814.1129762 Day | 0.9 N/m | Ds20x20 | Ds | 20 mm | #N/A | 20 mm | J200 | 32 mm | 44 mm | €43.75 | Alluminio | €270.00 | 120 N | 22 mm | 1.5 m/min | 77 | 100%
41031294 | 814.1129762 Day | 1.8 N/m | Ds20x20 | Ds | 20 mm | #N/A | 20 mm | J200 | 32 mm | 44 mm | €43.75 | Alluminio | €270.00 | 240 N | 11 mm | 0.8 m/min | 38.5 | 100%
31680329 | 628.5779563 Day | 0.7 N/m | Tr40x7 | Tr | 40 mm | #N/A | 7 mm | J | 67 mm | 70 mm | €64.52 | Acciaio inox | €424.90 | 80 N | 33 mm | 2.3 m/min | 330 | 100%
31680329 | 628.5779563 Day | 1.0 N/m | Tr40x7 | Tr | 40 mm | #N/A | 7 mm | J | 67 mm | 70 mm | €64.52 | Acciaio inox | €424.90 | 120 N | 22 mm | 1.5 m/min | 220 | 100%
31680329 | 628.5779563 Day | 1.9 N/m | Tr40x7 | Tr | 40 mm | #N/A | 7 mm | J | 67 mm | 70 mm | €64.52 | Acciaio inox | €424.90 | 240 N | 11 mm | 0.8 m/min | 110 | 100%
28983521 | 575.0698611 Day | 0.7 N/m | Ds18x24 | Ds | 18 mm | #N/A | 24 mm | J200 | 28 mm | 35 mm | €37.48 | Alluminio | €243.00 | 80 N | 33 mm | 2.3 m/min | 96.25 | 100%
28983521 | 575.0698611 Day | 1.0 N/m | Ds18x24 | Ds | 18 mm | #N/A | 24 mm | J200 | 28 mm | 35 mm | €37.48 | Alluminio | €243.00 | 120 N | 22 mm | 1.5 m/min | 64.16666667 | 100%
28983521 | 575.0698611 Day | 2.0 N/m | Ds18x24 | Ds | 18 mm | #N/A | 24 mm | J200 | 28 mm | 35 mm | €37.48 | Alluminio | €243.00 | 240 N | 11 mm | 0.8 m/min | 32.08333333 | 100%
27975883 | 555.0770437 Day | 2.2 N/m | Ds20x80 | Ds | 20 mm | #N/A | 80 mm | J200 | 32 mm | 44 mm | €45.08 | Alluminio | €270.00 | 80 N | 33 mm | 2.3 m/min | 28.875 | 100%
27975883 | 555.0770437 Day | 3.2 N/m | Ds20x80 | Ds | 20 mm | #N/A | 80 mm | J200 | 32 mm | 44 mm | €45.08 | Alluminio | €270.00 | 120 N | 22 mm | 1.5 m/min | 19.25 | 100%
27975883 | 555.0770437 Day | 6.4 N/m | Ds20x80 | Ds | 20 mm | #N/A | 80 mm | J200 | 32 mm | 44 mm | €45.08 | Alluminio | €270.00 | 240 N | 11 mm | 0.8 m/min | 9.625 | 100%
27881635 | 553.2070437 Day | 2.7 N/m | Ds20x90 | Ds | 20 mm | #N/A | 90 mm | J200 | 32 mm | 44 mm | €45.53 | Alluminio | €270.00 | 80 N | 33 mm | 2.3 m/min | 25.66666667 | 100%
27881635 | 553.2070437 Day | 1.7 N/m | Ds20x60 | Ds | 20 mm | #N/A | 60 mm | J200 | 32 mm | 44 mm | €44.63 | Alluminio | €270.00 | 80 N | 33 mm | 2.3 m/min | 38.5 | 100%
27881635 | 553.2070437 Day | 2.4 N/m | Ds20x60 | Ds | 20 mm | #N/A | 60 mm | J200 | 32 mm | 44 mm | €44.63 | Alluminio | €270.00 | 120 N | 22 mm | 1.5 m/min | 25.66666667 | 100%
27881635 | 553.2070437 Day | 4.0 N/m | Ds20x90 | Ds | 20 mm | #N/A | 90 mm | J200 | 32 mm | 44 mm | €45.53 | Alluminio | €270.00 | 120 N | 22 mm | 1.5 m/min | 17.11111111 | 100%
27881635 | 553.2070437 Day | 4.8 N/m | Ds20x60 | Ds | 20 mm | #N/A | 60 mm | J200 | 32 mm | 44 mm | €44.63 | Alluminio | €270.00 | 240 N | 11 mm | 0.8 m/min | 12.83333333 | 100%
27881635 | 553.2070437 Day | 7.9 N/m | Ds20x90 | Ds | 20 mm | #N/A | 90 mm | J200 | 32 mm | 44 mm | €45.53 | Alluminio | €270.00 | 240 N | 11 mm | 0.8 m/min | 8.555555556 | 100%
27517923 | 545.9905357 Day | 1.1 N/m | Ds18x40 | Ds | 18 mm | #N/A | 40 mm | J200 | 28 mm | 35 mm | €37.86 | Alluminio | €243.00 | 80 N | 33 mm | 2.3 m/min | 57.75 | 100%
27517923 | 545.9905357 Day | 1.6 N/m | Ds18x40 | Ds | 18 mm | #N/A | 40 mm | J200 | 28 mm | 35 mm | €37.86 | Alluminio | €243.00 | 120 N | 22 mm | 1.5 m/min | 38.5 | 100%
27517923 | 545.9905357 Day | 3.1 N/m | Ds18x40 | Ds | 18 mm | #N/A | 40 mm | J200 | 28 mm | 35 mm | €37.86 | Alluminio | €243.00 | 240 N | 11 mm | 0.8 m/min | 19.25 | 100%
24543693 | 486.9780357 Day | 0.6 N/m | Tr36x6 | Tr | 36 mm | #N/A | 6 mm | J | 67 mm | 70 mm | €55.76 | Acciaio inox | €332.90 | 80 N | 33 mm | 2.3 m/min | 385 | 100%
24543693 | 486.9780357 Day | 0.9 N/m | Tr36x6 | Tr | 36 mm | #N/A | 6 mm | J | 67 mm | 70 mm | €55.76 | Acciaio inox | €332.90 | 120 N | 22 mm | 1.5 m/min | 256.6666667 | 100%
24543693 | 486.9780357 Day | 1.7 N/m | Tr36x6 | Tr | 36 mm | #N/A | 6 mm | J | 67 mm | 70 mm | €55.76 | Acciaio inox | €332.90 | 240 N | 11 mm | 0.8 m/min | 128.3333333 | 100%
24120954 | 478.5903571 Day | 0.9 N/m | Ds16x35 | Ds | 16 mm | #N/A | 35 mm | J200 | 28 mm | 35 mm | €37.11 | Alluminio | €243.00 | 80 N | 33 mm | 2.3 m/min | 66 | 100%
24120954 | 478.5903571 Day | 1.4 N/m | Ds16x35 | Ds | 16 mm | #N/A | 35 mm | J200 | 28 mm | 35 mm | €37.11 | Alluminio | €243.00 | 120 N | 22 mm | 1.5 m/min | 44 | 100%
24120954 | 478.5903571 Day | 2.7 N/m | Ds16x35 | Ds | 16 mm | #N/A | 35 mm | J200 | 28 mm | 35 mm | €37.11 | Alluminio | €243.00 | 240 N | 11 mm | 0.8 m/min | 22 | 100%
22176230 | 440.0045635 Day | 0.7 N/m | Tr40x7 | Tr | 40 mm | #N/A | 7 mm | J | 67 mm | 70 mm | €64.52 | Acciaio C15 | €93.70 | 80 N | 33 mm | 2.3 m/min | 330 | 100%
22176230 | 440.0045635 Day | 1.0 N/m | Tr40x7 | Tr | 40 mm | #N/A | 7 mm | J | 67 mm | 70 mm | €64.52 | Acciaio C15 | €93.70 | 120 N | 22 mm | 1.5 m/min | 220 | 100%
22176230 | 440.0045635 Day | 1.9 N/m | Tr40x7 | Tr | 40 mm | #N/A | 7 mm | J | 67 mm | 70 mm | €64.52 | Acciaio C15 | €93.70 | 240 N | 11 mm | 0.8 m/min | 110 | 100%
20877573 | 414.2375595 Day | 2.4 N/m | Ds18x80 | Ds | 18 mm | #N/A | 80 mm | J200 | 28 mm | 35 mm | €38.04 | Alluminio | €310.50 | 80 N | 33 mm | 2.3 m/min | 28.875 | 100%
20877573 | 414.2375595 Day | 3.5 N/m | Ds18x80 | Ds | 18 mm | #N/A | 80 mm | J200 | 28 mm | 35 mm | €38.04 | Alluminio | €310.50 | 120 N | 22 mm | 1.5 m/min | 19.25 | 100%
20877573 | 414.2375595 Day | 7.0 N/m | Ds18x80 | Ds | 18 mm | #N/A | 80 mm | J200 | 28 mm | 35 mm | €38.04 | Alluminio | €310.50 | 240 N | 11 mm | 0.8 m/min | 9.625 | 100%
17180585 | 340.884623 Day | 0.6 N/m | Tr36x6 | Tr | 36 mm | #N/A | 6 mm | J | 67 mm | 70 mm | €55.76 | Acciaio C15 | €75.30 | 80 N | 33 mm | 2.3 m/min | 385 | 100%
17180585 | 340.884623 Day | 0.9 N/m | Tr36x6 | Tr | 36 mm | #N/A | 6 mm | J | 67 mm | 70 mm | €55.76 | Acciaio C15 | €75.30 | 120 N | 22 mm | 1.5 m/min | 256.6666667 | 100%
17180585 | 340.884623 Day | 1.7 N/m | Tr36x6 | Tr | 36 mm | #N/A | 6 mm | J | 67 mm | 70 mm | €55.76 | Acciaio C15 | €75.30 | 240 N | 11 mm | 0.8 m/min | 128.3333333 | 100%
16627827 | 329.9172024 Day | 3.0 N/m | Ds18x100 | Ds | 18 mm | #N/A | 100 mm | J200 | 28 mm | 35 mm | €38.22 | Alluminio | €243.00 | 80 N | 33 mm | 2.3 m/min | 23.1 | 100%
16627827 | 329.9172024 Day | 4.5 N/m | Ds18x100 | Ds | 18 mm | #N/A | 100 mm | J200 | 28 mm | 35 mm | €38.22 | Alluminio | €243.00 | 120 N | 22 mm | 1.5 m/min | 15.4 | 100%
16627827 | 329.9172024 Day | 8.9 N/m | Ds18x100 | Ds | 18 mm | #N/A | 100 mm | J200 | 28 mm | 35 mm | €38.22 | Alluminio | €243.00 | 240 N | 11 mm | 0.8 m/min | 7.7 | 100%
14173717 | 281.2245437 Day | 0.8 N/m | Tr32x6 | Tr | 32 mm | #N/A | 6 mm | J | 45 mm | 46 mm | €33.87 | Acciaio inox | €346.70 | 120 N | 22 mm | 1.5 m/min | 256.6666667 | 100%
14173717 | 281.2245437 Day | 1.5 N/m | Tr32x6 | Tr | 32 mm | #N/A | 6 mm | J | 45 mm | 46 mm | €33.87 | Acciaio inox | €346.70 | 240 N | 11 mm | 0.8 m/min | 128.3333333 | 100%
13196219 | 261.8297421 Day | 0.5 N/m | Tr30x6 | Tr | 30 mm | #N/A | 6 mm | J | 38 mm | 46 mm | €29.79 | Acciaio inox | €240.90 | 80 N | 33 mm | 2.3 m/min | 385 | 100%
13196219 | 261.8297421 Day | 0.5 N/m | Tr30x6 | Tr | 30 mm | #N/A | 6 mm | J | 45 mm | 46 mm | €33.87 | Acciaio inox | €240.90 | 80 N | 33 mm | 2.3 m/min | 385 | 100%
13196219 | 261.8297421 Day | 0.8 N/m | Tr30x6 | Tr | 30 mm | #N/A | 6 mm | J | 38 mm | 46 mm | €29.79 | Acciaio inox | €240.90 | 120 N | 22 mm | 1.5 m/min | 256.6666667 | 100%
13196219 | 261.8297421 Day | 0.8 N/m | Tr30x6 | Tr | 30 mm | #N/A | 6 mm | J | 45 mm | 46 mm | €33.87 | Acciaio inox | €240.90 | 120 N | 22 mm | 1.5 m/min | 256.6666667 | 100%
13196219 | 261.8297421 Day | 1.5 N/m | Tr30x6 | Tr | 30 mm | #N/A | 6 mm | J | 38 mm | 46 mm | €29.79 | Acciaio inox | €240.90 | 240 N | 11 mm | 0.8 m/min | 128.3333333 | 100%
13196219 | 261.8297421 Day | 1.5 N/m | Tr30x6 | Tr | 30 mm | #N/A | 6 mm | J | 45 mm | 46 mm | €33.87 | Acciaio inox | €240.90 | 240 N | 11 mm | 0.8 m/min | 128.3333333 | 100%
12567828 | 249.3616667 Day | 0.5 N/m | Tr30x6 | Tr | 30 mm | #N/A | 6 mm | W300 | 38 mm | 46 mm | €37.39 | Acciaio inox | €240.90 | 80 N | 33 mm | 2.3 m/min | 385 | 100%
12567828 | 249.3616667 Day | 0.5 N/m | Tr30x6 | Tr | 30 mm | #N/A | 6 mm | W300 | 45 mm | 46 mm | €43.40 | Acciaio inox | €240.90 | 80 N | 33 mm | 2.3 m/min | 385 | 100%
12567828 | 249.3616667 Day | 0.8 N/m | Tr30x6 | Tr | 30 mm | #N/A | 6 mm | W300 | 38 mm | 46 mm | €37.39 | Acciaio inox | €240.90 | 120 N | 22 mm | 1.5 m/min | 256.6666667 | 100%
12567828 | 249.3616667 Day | 0.8 N/m | Tr30x6 | Tr | 30 mm | #N/A | 6 mm | W300 | 45 mm | 46 mm | €43.40 | Acciaio inox | €240.90 | 120 N | 22 mm | 1.5 m/min | 256.6666667 | 100%
12567828 | 249.3616667 Day | 1.5 N/m | Tr30x6 | Tr | 30 mm | #N/A | 6 mm | W300 | 38 mm | 46 mm | €37.39 | Acciaio inox | €240.90 | 240 N | 11 mm | 0.8 m/min | 128.3333333 | 100%
12567828 | 249.3616667 Day | 1.5 N/m | Tr30x6 | Tr | 30 mm | #N/A | 6 mm | W300 | 45 mm | 46 mm | €43.40 | Acciaio inox | €240.90 | 240 N | 11 mm | 0.8 m/min | 128.3333333 | 100%
11225584 | 222.7298413 Day | 0.4 N/m | Tr20x4 | Tr | 20 mm | #N/A | 4 mm | J200 | 32 mm | 44 mm | €37.82 | Alluminio | €255.00 | 80 N | 33 mm | 2.3 m/min | 577.5 | 100%
11225584 | 222.7298413 Day | 0.5 N/m | Tr20x4 | Tr | 20 mm | #N/A | 4 mm | J200 | 32 mm | 44 mm | €37.82 | Alluminio | €255.00 | 120 N | 22 mm | 1.5 m/min | 385 | 100%
11225584 | 222.7298413 Day | 1.0 N/m | Tr20x4 | Tr | 20 mm | #N/A | 4 mm | J200 | 32 mm | 44 mm | €37.82 | Alluminio | €255.00 | 240 N | 11 mm | 0.8 m/min | 192.5 | 100%
10381759 | 205.9872817 Day | 0.5 N/m | Tr28x5 | Tr | 28 mm | #N/A | 5 mm | J | 38 mm | 46 mm | €25.10 | Acciaio inox | €194.90 | 80 N | 33 mm | 2.3 m/min | 462 | 100%
10381759 | 205.9872817 Day | 0.7 N/m | Tr28x5 | Tr | 28 mm | #N/A | 5 mm | J | 38 mm | 46 mm | €25.10 | Acciaio inox | €194.90 | 120 N | 22 mm | 1.5 m/min | 308 | 100%
10381759 | 205.9872817 Day | 1.3 N/m | Tr28x5 | Tr | 28 mm | #N/A | 5 mm | J | 38 mm | 46 mm | €25.10 | Acciaio inox | €194.90 | 240 N | 11 mm | 0.8 m/min | 154 | 100%
10257824 | 203.528254 Day | 0.6 N/m | Ds20x20 | Ds | 20 mm | #N/A | 20 mm | J | 32 mm | 44 mm | €33.28 | Alluminio | €270.00 | 80 N | 33 mm | 2.3 m/min | 115.5 | 100%
10257824 | 203.528254 Day | 0.6 N/m | Ds20x20 | Ds | 20 mm | #N/A | 20 mm | J | 32 mm | 44 mm | €33.28 | Acciaio inox | €154.98 | 80 N | 33 mm | 2.3 m/min | 115.5 | 100%
10257824 | 203.528254 Day | 0.9 N/m | Ds20x20 | Ds | 20 mm | #N/A | 20 mm | J | 32 mm | 44 mm | €33.28 | Alluminio | €270.00 | 120 N | 22 mm | 1.5 m/min | 77 | 100%
10257824 | 203.528254 Day | 0.9 N/m | Ds20x20 | Ds | 20 mm | #N/A | 20 mm | J | 32 mm | 44 mm | €33.28 | Acciaio inox | €154.98 | 120 N | 22 mm | 1.5 m/min | 77 | 100%
10257824 | 203.528254 Day | 1.8 N/m | Ds20x20 | Ds | 20 mm | #N/A | 20 mm | J | 32 mm | 44 mm | €33.28 | Alluminio | €270.00 | 240 N | 11 mm | 0.8 m/min | 38.5 | 100%
10257824 | 203.528254 Day | 1.8 N/m | Ds20x20 | Ds | 20 mm | #N/A | 20 mm | J | 32 mm | 44 mm | €33.28 | Acciaio inox | €154.98 | 240 N | 11 mm | 0.8 m/min | 38.5 | 100%
9921602 | 196.8571825 Day | 0.8 N/m | Tr32x6 | Tr | 32 mm | #N/A | 6 mm | J | 45 mm | 46 mm | €33.87 | Acciaio C15 | €67.48 | 120 N | 22 mm | 1.5 m/min | 256.6666667 | 100%
9921602 | 196.8571825 Day | 1.5 N/m | Tr32x6 | Tr | 32 mm | #N/A | 6 mm | J | 45 mm | 46 mm | €33.87 | Acciaio C15 | €67.48 | 240 N | 11 mm | 0.8 m/min | 128.3333333 | 100%
9887389 | 196.1783532 Day | 0.5 N/m | Tr28x5 | Tr | 28 mm | #N/A | 5 mm | W300 | 38 mm | 46 mm | €32.18 | Acciaio inox | €194.90 | 80 N | 33 mm | 2.3 m/min | 462 | 100%
9887389 | 196.1783532 Day | 0.7 N/m | Tr28x5 | Tr | 28 mm | #N/A | 5 mm | W300 | 38 mm | 46 mm | €32.18 | Acciaio inox | €194.90 | 120 N | 22 mm | 1.5 m/min | 308 | 100%
9887389 | 196.1783532 Day | 1.3 N/m | Tr28x5 | Tr | 28 mm | #N/A | 5 mm | W300 | 38 mm | 46 mm | €32.18 | Acciaio inox | €194.90 | 240 N | 11 mm | 0.8 m/min | 154 | 100%
9567503 | 189.8314087 Day | 0.5 N/m | Tr26x5 | Tr | 26 mm | #N/A | 5 mm | J | 38 mm | 46 mm | €24.06 | Acciaio inox | €171.90 | 80 N | 33 mm | 2.3 m/min | 462 | 100%
9567503 | 189.8314087 Day | 0.7 N/m | Tr26x5 | Tr | 26 mm | #N/A | 5 mm | J | 38 mm | 46 mm | €24.06 | Acciaio inox | €171.90 | 120 N | 22 mm | 1.5 m/min | 308 | 100%
9567503 | 189.8314087 Day | 1.3 N/m | Tr26x5 | Tr | 26 mm | #N/A | 5 mm | J | 38 mm | 46 mm | €24.06 | Acciaio inox | €171.90 | 240 N | 11 mm | 0.8 m/min | 154 | 100%
9237353 | 183.2808135 Day | 0.5 N/m | Tr30x6 | Tr | 30 mm | #N/A | 6 mm | J | 38 mm | 46 mm | €29.79 | Acciaio C15 | €54.60 | 80 N | 33 mm | 2.3 m/min | 385 | 100%
9237353 | 183.2808135 Day | 0.5 N/m | Tr30x6 | Tr | 30 mm | #N/A | 6 mm | J | 45 mm | 46 mm | €33.87 | Acciaio C15 | €54.60 | 80 N | 33 mm | 2.3 m/min | 385 | 100%
9237353 | 183.2808135 Day | 0.8 N/m | Tr30x6 | Tr | 30 mm | #N/A | 6 mm | J | 38 mm | 46 mm | €29.79 | Acciaio C15 | €54.60 | 120 N | 22 mm | 1.5 m/min | 256.6666667 | 100%
9237353 | 183.2808135 Day | 0.8 N/m | Tr30x6 | Tr | 30 mm | #N/A | 6 mm | J | 45 mm | 46 mm | €33.87 | Acciaio C15 | €54.60 | 120 N | 22 mm | 1.5 m/min | 256.6666667 | 100%
9237353 | 183.2808135 Day | 1.5 N/m | Tr30x6 | Tr | 30 mm | #N/A | 6 mm | J | 38 mm | 46 mm | €29.79 | Acciaio C15 | €54.60 | 240 N | 11 mm | 0.8 m/min | 128.3333333 | 100%
9237353 | 183.2808135 Day | 1.5 N/m | Tr30x6 | Tr | 30 mm | #N/A | 6 mm | J | 45 mm | 46 mm | €33.87 | Acciaio C15 | €54.60 | 240 N | 11 mm | 0.8 m/min | 128.3333333 | 100%
9111908 | 180.7918254 Day | 0.5 N/m | Tr26x5 | Tr | 26 mm | #N/A | 5 mm | W300 | 38 mm | 46 mm | €31.02 | Acciaio inox | €171.90 | 80 N | 33 mm | 2.3 m/min | 462 | 100%
9111908 | 180.7918254 Day | 0.7 N/m | Tr26x5 | Tr | 26 mm | #N/A | 5 mm | W300 | 38 mm | 46 mm | €31.02 | Acciaio inox | €171.90 | 120 N | 22 mm | 1.5 m/min | 308 | 100%
9111908 | 180.7918254 Day | 1.3 N/m | Tr26x5 | Tr | 26 mm | #N/A | 5 mm | W300 | 38 mm | 46 mm | €31.02 | Acciaio inox | €171.90 | 240 N | 11 mm | 0.8 m/min | 154 | 100%
8797479 | 174.5531548 Day | 0.5 N/m | Tr30x6 | Tr | 30 mm | #N/A | 6 mm | W300 | 38 mm | 46 mm | €37.39 | Acciaio C15 | €54.60 | 80 N | 33 mm | 2.3 m/min | 385 | 100%
8797479 | 174.5531548 Day | 0.5 N/m | Tr30x6 | Tr | 30 mm | #N/A | 6 mm | W300 | 45 mm | 46 mm | €43.40 | Acciaio C15 | €54.60 | 80 N | 33 mm | 2.3 m/min | 385 | 100%
8797479 | 174.5531548 Day | 0.8 N/m | Tr30x6 | Tr | 30 mm | #N/A | 6 mm | W300 | 38 mm | 46 mm | €37.39 | Acciaio C15 | €54.60 | 120 N | 22 mm | 1.5 m/min | 256.6666667 | 100%
8797479 | 174.5531548 Day | 0.8 N/m | Tr30x6 | Tr | 30 mm | #N/A | 6 mm | W300 | 45 mm | 46 mm | €43.40 | Acciaio C15 | €54.60 | 120 N | 22 mm | 1.5 m/min | 256.6666667 | 100%
8797479 | 174.5531548 Day | 1.5 N/m | Tr30x6 | Tr | 30 mm | #N/A | 6 mm | W300 | 38 mm | 46 mm | €37.39 | Acciaio C15 | €54.60 | 240 N | 11 mm | 0.8 m/min | 128.3333333 | 100%
8797479 | 174.5531548 Day | 1.5 N/m | Tr30x6 | Tr | 30 mm | #N/A | 6 mm | W300 | 45 mm | 46 mm | €43.40 | Acciaio C15 | €54.60 | 240 N | 11 mm | 0.8 m/min | 128.3333333 | 100%
8372672 | 166.1244444 Day | 0.4 N/m | Tr24x5 | Tr | 24 mm | #N/A | 5 mm | J | 32 mm | 44 mm | €17.69 | Acciaio inox | €147.52 | 80 N | 33 mm | 2.3 m/min | 462 | 100%
8372672 | 166.1244444 Day | 0.6 N/m | Tr24x5 | Tr | 24 mm | #N/A | 5 mm | J | 32 mm | 44 mm | €17.69 | Acciaio inox | €147.52 | 120 N | 22 mm | 1.5 m/min | 308 | 100%
8372672 | 166.1244444 Day | 1.2 N/m | Tr24x5 | Tr | 24 mm | #N/A | 5 mm | J | 32 mm | 44 mm | €17.69 | Acciaio inox | €147.52 | 240 N | 11 mm | 0.8 m/min | 154 | 100%
7973973 | 158.21375 Day | 0.4 N/m | Tr24x5 | Tr | 24 mm | #N/A | 5 mm | W300 | 32 mm | 44 mm | €24.23 | Acciaio inox | €147.52 | 80 N | 33 mm | 2.3 m/min | 462 | 100%
7973973 | 158.21375 Day | 0.6 N/m | Tr24x5 | Tr | 24 mm | #N/A | 5 mm | W300 | 32 mm | 44 mm | €24.23 | Acciaio inox | €147.52 | 120 N | 22 mm | 1.5 m/min | 308 | 100%
7973973 | 158.21375 Day | 1.2 N/m | Tr24x5 | Tr | 24 mm | #N/A | 5 mm | W300 | 32 mm | 44 mm | €24.23 | Acciaio inox | €147.52 | 240 N | 11 mm | 0.8 m/min | 154 | 100%
7937281 | 157.4857341 Day | 0.4 N/m | Tr18x4 | Tr | 18 mm | #N/A | 4 mm | J200 | 28 mm | 35 mm | €36.35 | Alluminio | €177.48 | 80 N | 33 mm | 2.3 m/min | 577.5 | 100%
7937281 | 157.4857341 Day | 0.5 N/m | Tr18x4 | Tr | 18 mm | #N/A | 4 mm | J200 | 28 mm | 35 mm | €36.35 | Alluminio | €177.48 | 120 N | 22 mm | 1.5 m/min | 385 | 100%
7937281 | 157.4857341 Day | 1.0 N/m | Tr18x4 | Tr | 18 mm | #N/A | 4 mm | J200 | 28 mm | 35 mm | €36.35 | Alluminio | €177.48 | 240 N | 11 mm | 0.8 m/min | 192.5 | 100%
7711671 | 153.0093452 Day | 0.4 N/m | Tr24x5 | Tr | 24 mm | #N/A | 5 mm | R | 32 mm | 44 mm | €15.06 | Acciaio inox | €147.52 | 80 N | 33 mm | 2.3 m/min | 462 | 100%
7711671 | 153.0093452 Day | 0.6 N/m | Tr24x5 | Tr | 24 mm | #N/A | 5 mm | R | 32 mm | 44 mm | €15.06 | Acciaio inox | €147.52 | 120 N | 22 mm | 1.5 m/min | 308 | 100%
7711671 | 153.0093452 Day | 1.2 N/m | Tr24x5 | Tr | 24 mm | #N/A | 5 mm | R | 32 mm | 44 mm | €15.06 | Acciaio inox | €147.52 | 240 N | 11 mm | 0.8 m/min | 154 | 100%
7267231 | 144.1910913 Day | 0.5 N/m | Tr28x5 | Tr | 28 mm | #N/A | 5 mm | J | 38 mm | 46 mm | €25.10 | Acciaio C15 | €56.90 | 80 N | 33 mm | 2.3 m/min | 462 | 100%
7267231 | 144.1910913 Day | 0.7 N/m | Tr28x5 | Tr | 28 mm | #N/A | 5 mm | J | 38 mm | 46 mm | €25.10 | Acciaio C15 | €56.90 | 120 N | 22 mm | 1.5 m/min | 308 | 100%
7267231 | 144.1910913 Day | 1.3 N/m | Tr28x5 | Tr | 28 mm | #N/A | 5 mm | J | 38 mm | 46 mm | €25.10 | Acciaio C15 | €56.90 | 240 N | 11 mm | 0.8 m/min | 154 | 100%
7245880 | 143.7674603 Day | 0.7 N/m | Ds18x24 | Ds | 18 mm | #N/A | 24 mm | J | 28 mm | 35 mm | €26.91 | Alluminio | €243.00 | 80 N | 33 mm | 2.3 m/min | 96.25 | 100%
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

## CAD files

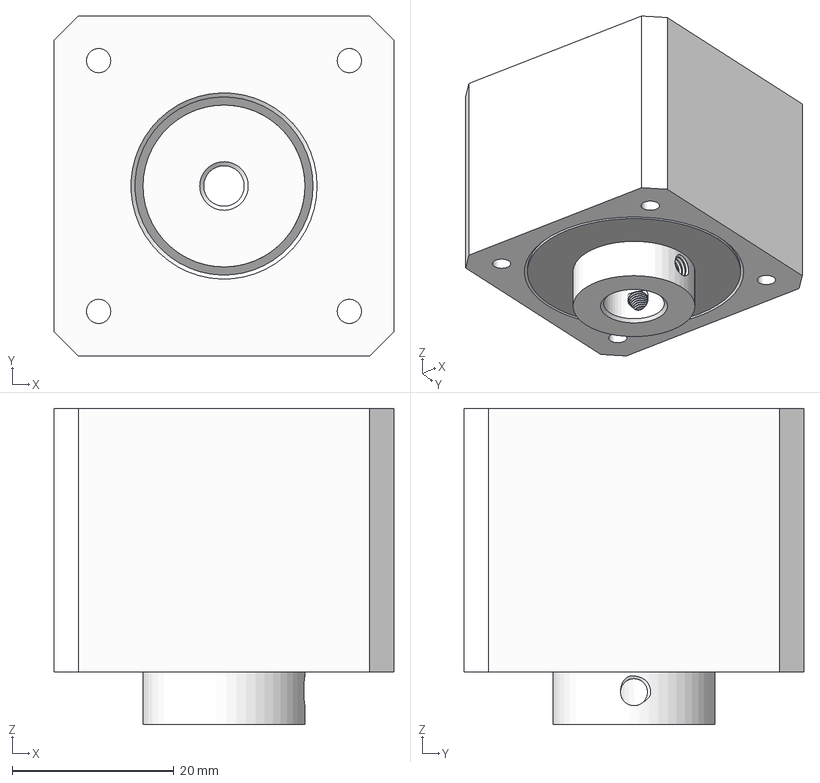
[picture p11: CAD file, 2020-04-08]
src/CAD/ASSY/A05_OB_200327.step
42.0 x 42.0 x 39.1 mm
5909K75 x 4
5909K15 x 2
HI_GFM-2023-11
P0008_OB_200327
P0005_OB_200326

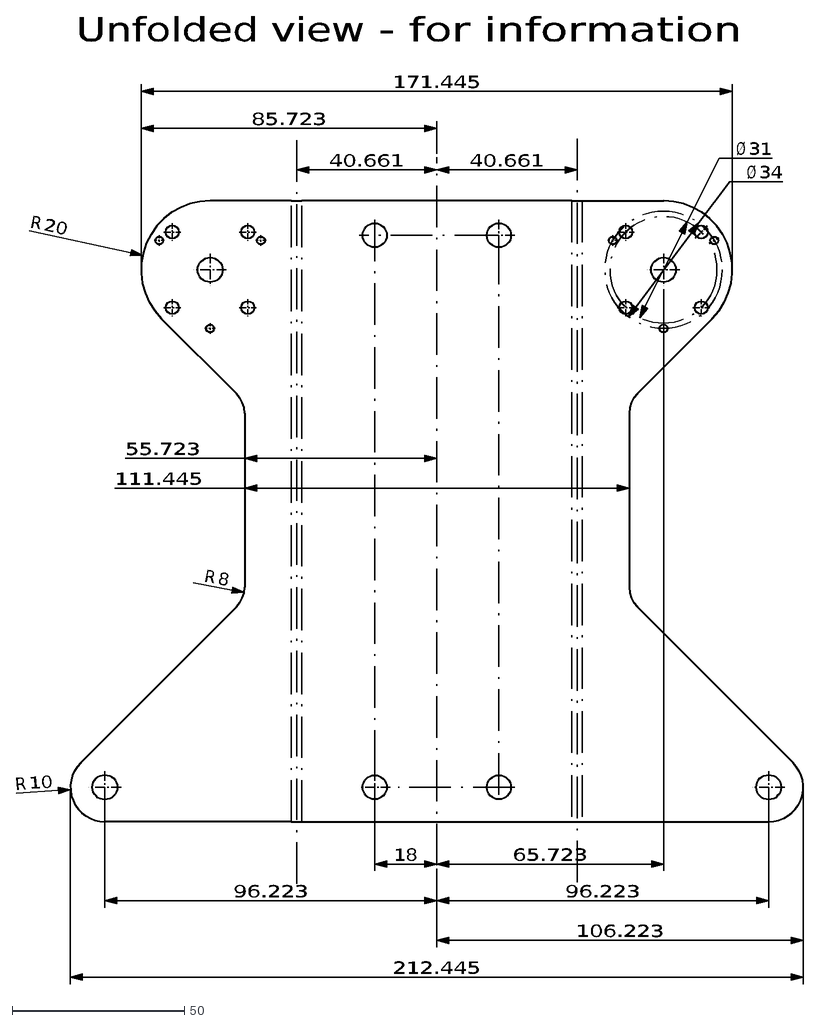
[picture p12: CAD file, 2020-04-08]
src/CAD/DXF/P0001_OB_200326.dxf
Unfolded view
- for information
18
96.223
65.723
34
Ø
31
10
R
20
40.661
85.723
106.223
212.445
171.445
55.723
111.445
8

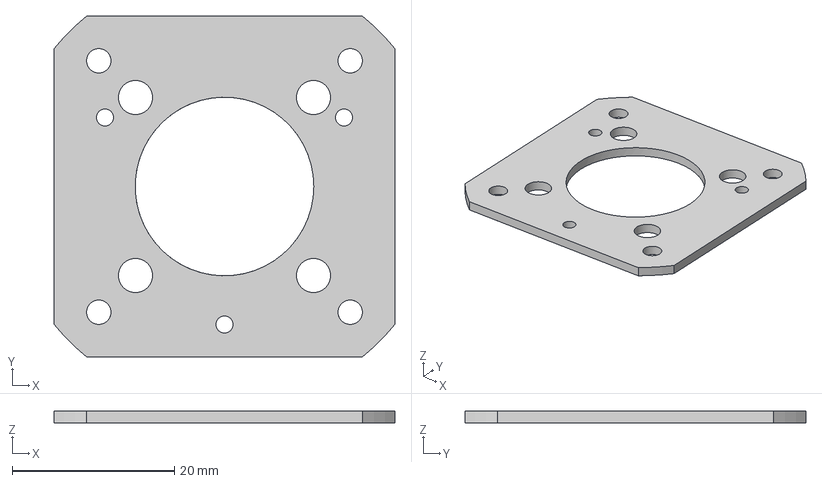
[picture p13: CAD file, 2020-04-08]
src/CAD/PARTS/P0009_OB_200326.step
42.0 x 42.0 x 1.50 mm

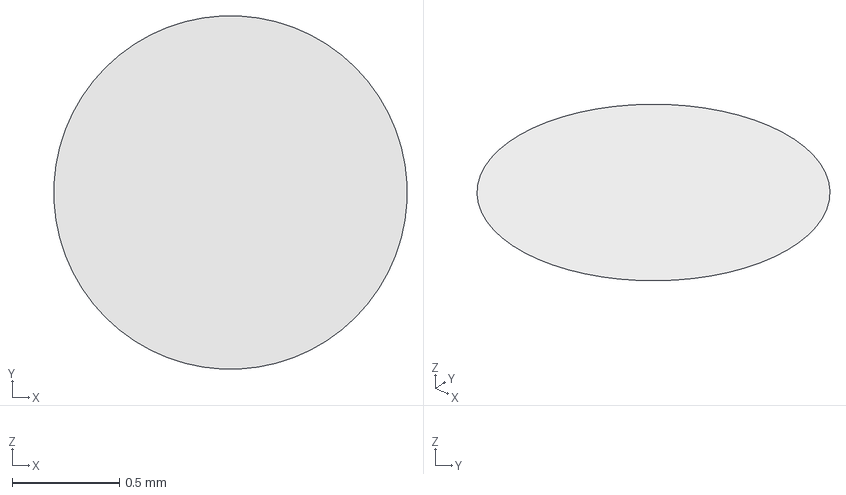
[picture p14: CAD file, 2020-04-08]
src/Hardware/Encoder Board/production/motor_encoder_brd.stp
1.65 x 1.65 x 0 mm

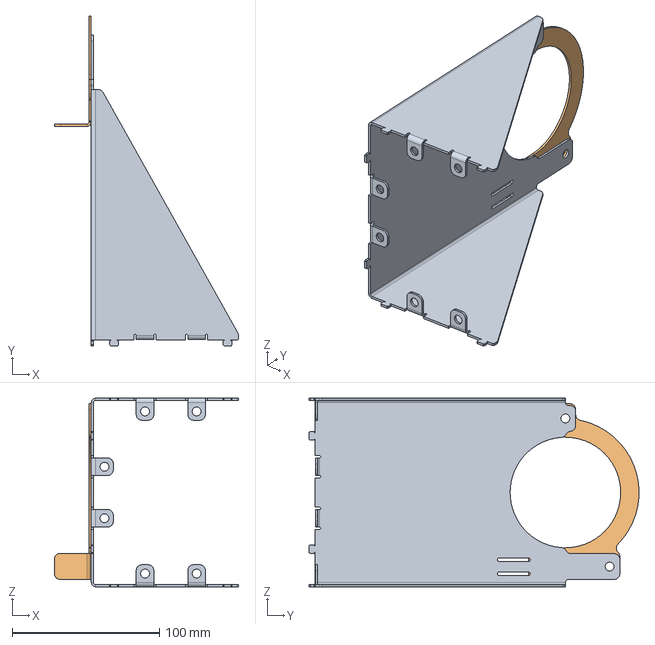
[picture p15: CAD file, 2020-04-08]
src/CAD/ASSY/A06_OB_200328_WO_SmallParts.iges
125.0 x 223.9 x 128.0 mm

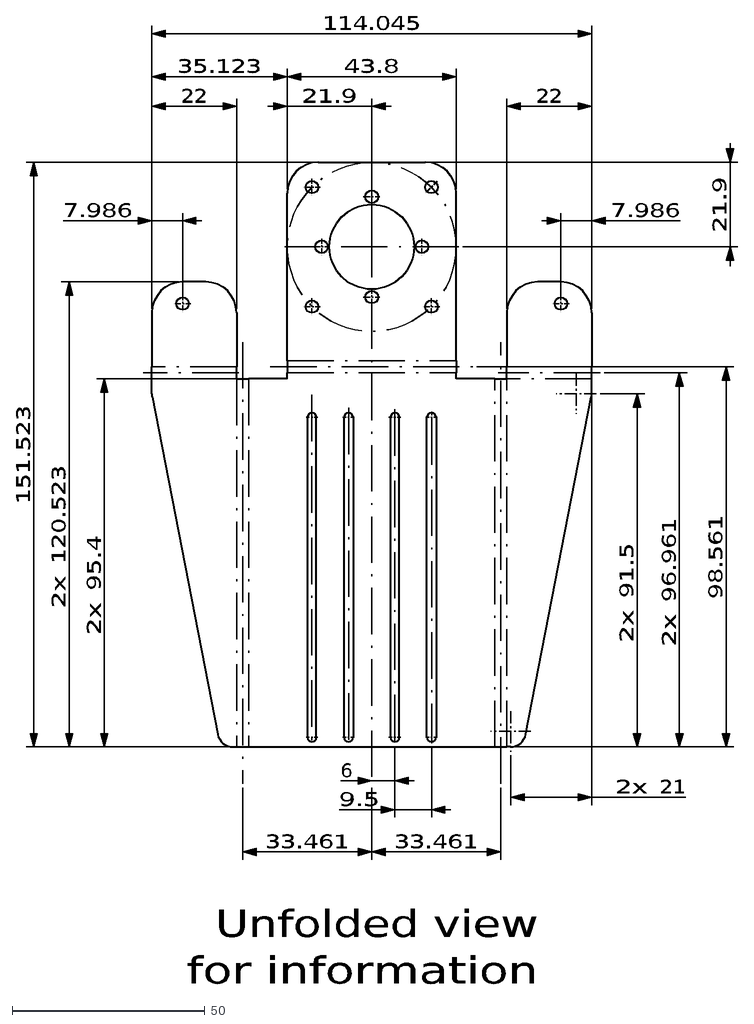
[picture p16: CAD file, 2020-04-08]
src/CAD/DXF/P0010_OB_200328.dxf
Unfolded view
for information
114.045
151.523
22
35.123
43.8
21.9
95.4
2x
120.523
7.986
21
91.5
6
9.5
33.461
96.961
98.561

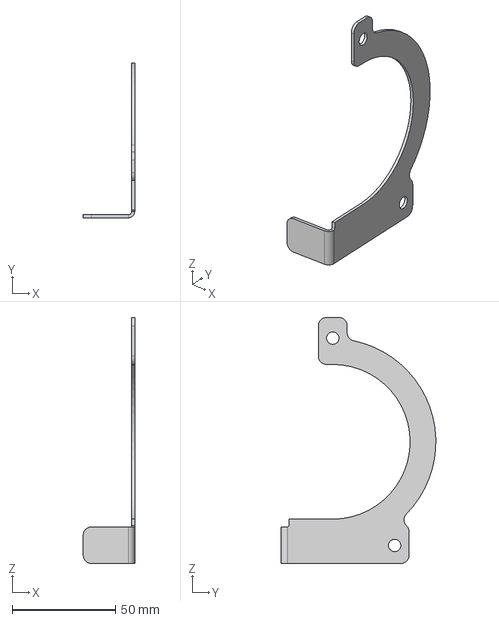
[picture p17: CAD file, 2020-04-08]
src/CAD/PARTS/P0012_OB_200328.step
25.0 x 75.0 x 119.2 mm

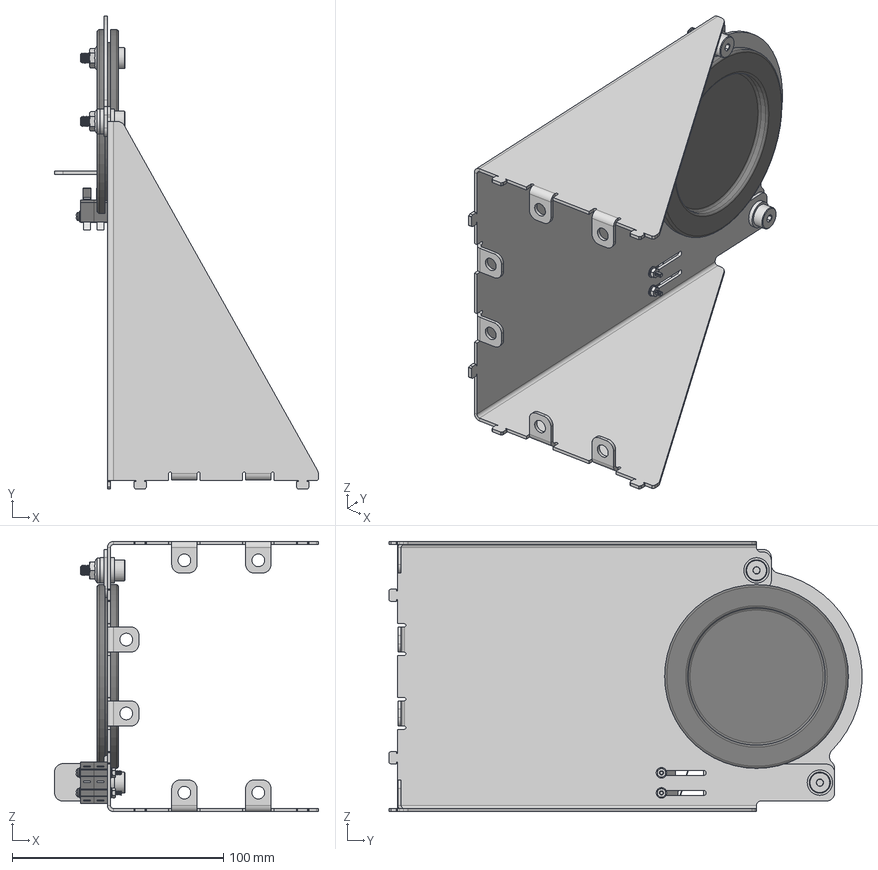
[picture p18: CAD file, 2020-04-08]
src/CAD/ASSY/A06_OB_200328.step
125.0 x 223.9 x 128.0 mm
HELAVIA DG M75
P0011_OB_200328
P0012_OB_200328
98687A111 x 4
92981A148 x 2
90374A111 x 2
Omron_LimitSwitch_20834 x 2
93475A195 x 4
92000A026 x 2
90592A075 x 2

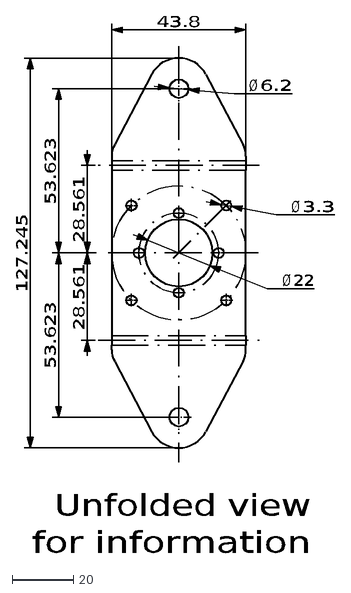
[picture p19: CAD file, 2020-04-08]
src/CAD/DXF/P0002_OB_200326.dxf
Unfolded view
for information
3.3
Ø
22
6.2
43.8
127.245
28.561
53.623

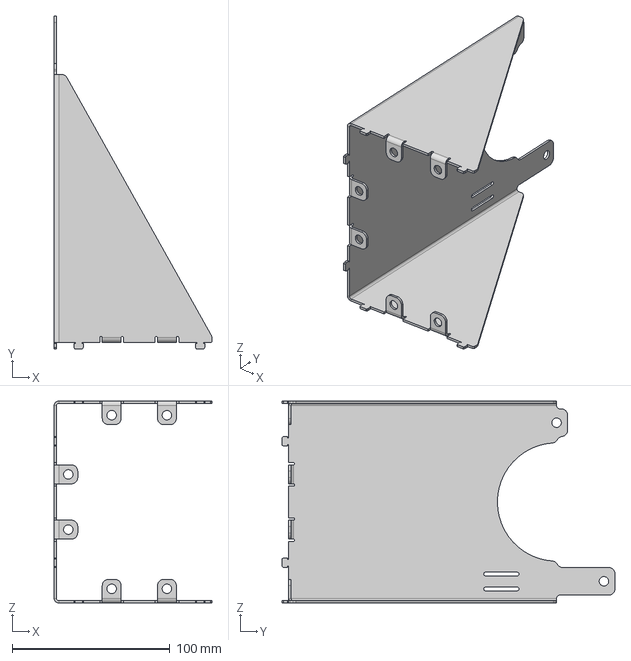
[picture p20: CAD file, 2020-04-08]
src/CAD/PARTS/P0011_OB_200328.step
100.0 x 211.0 x 128.0 mm

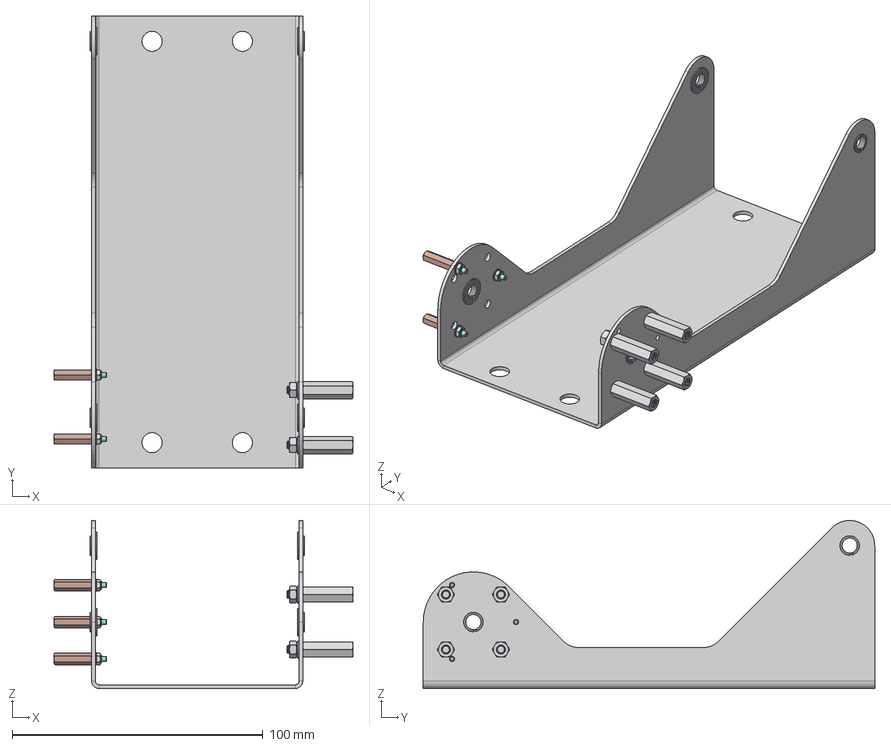
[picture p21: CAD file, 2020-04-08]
src/CAD/ASSY/A01_OB_200326.step
119.2 x 180.0 x 67.0 mm
MCM_06_015_1 x 4
P0001_OB_200326
93655A429 x 4
98688A113 x 4
90592A104 x 4
93475A195 x 3
90592A075 x 3
WE_Standoffs_M2_15_971150244 x 3

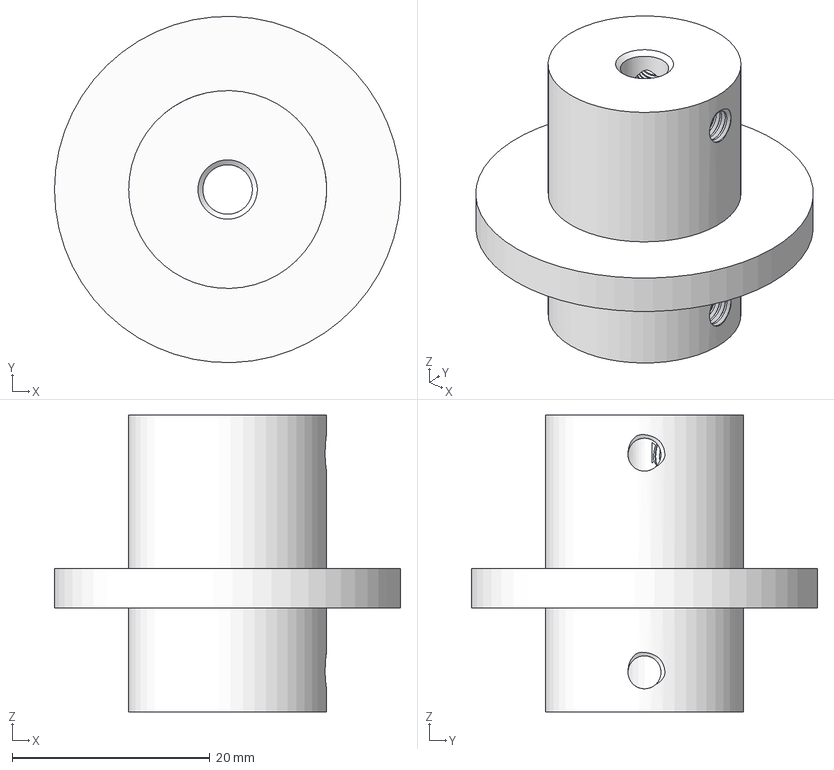
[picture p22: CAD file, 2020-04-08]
src/CAD/PARTS/P0005_OB_200326.step
35.0 x 35.0 x 30.0 mm

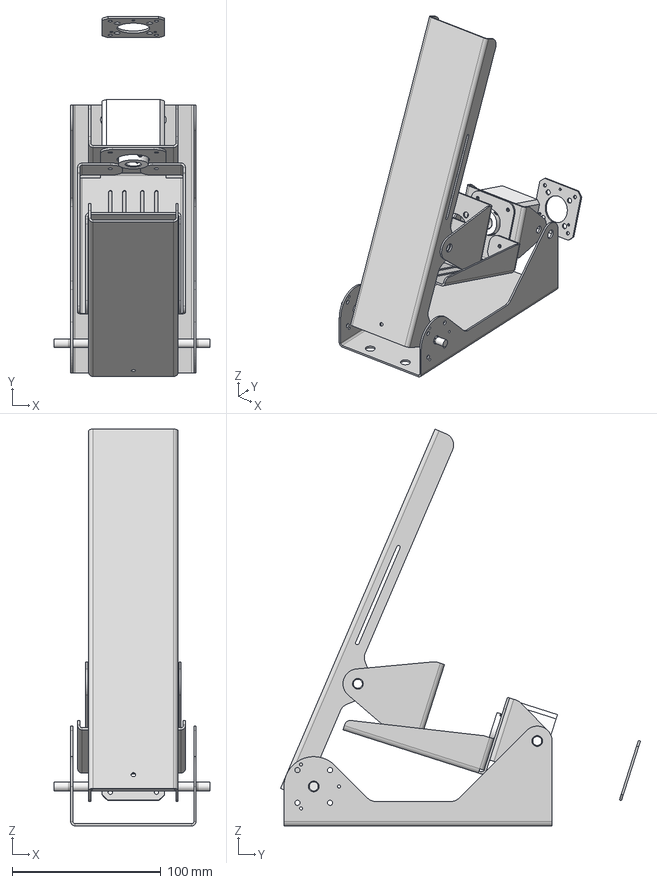
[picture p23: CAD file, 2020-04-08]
src/CAD/ASSY/A02_OB_200326_WO_SmallParts.step
104.5 x 241.6 x 266.4 mm
P0001_OB_200326
P0002_OB_200326
P0005_OB_200326
P0008_OB_200327
P0009_OB_200326
P0010_OB_200328
P0003_OB_200326
P0004_OB_200326
P0007_OB_200327

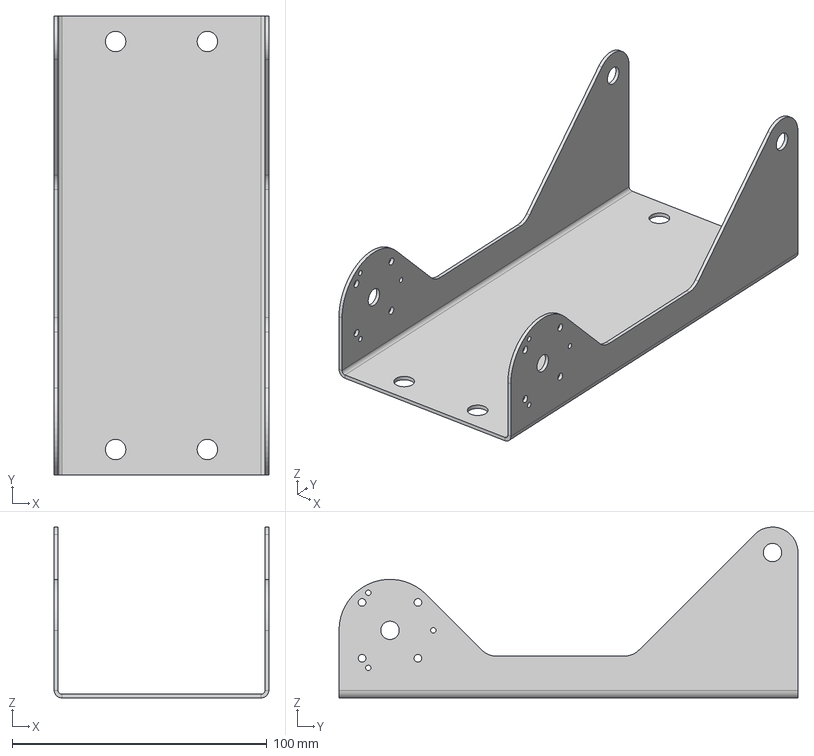
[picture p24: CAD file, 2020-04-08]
src/CAD/PARTS/P0001_OB_200331_r02.step
84.2 x 180.0 x 67.0 mm

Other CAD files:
src/CAD/ASSY/A04_OB_200326.step
src/CAD/PARTS/P0010_OB_200328_r02.step
src/CAD/PARTS/P0003_OB_200326.step
src/CAD/PARTS/P0006_OB_200327.step
src/CAD/DXF/P0003_OB_200326.dxf
src/CAD/DXF/P0004_OB_200326.dxf
src/CAD/DXF/P0006_OB_200327.dxf
src/CAD/DXF/P0009_OB_200326.dxf
src/CAD/DXF/P0011_OB_200328.dxf
src/CAD/DXF/P0012_OB_200328.dxf
src/CAD/PARTS/P0002_OB_200331_r02.step
src/CAD/PARTS/P0004_OB_200326.step
src/CAD/PARTS/P0007_OB_200327.step
src/CAD/PARTS/P0008_OB_200331_r03.step
